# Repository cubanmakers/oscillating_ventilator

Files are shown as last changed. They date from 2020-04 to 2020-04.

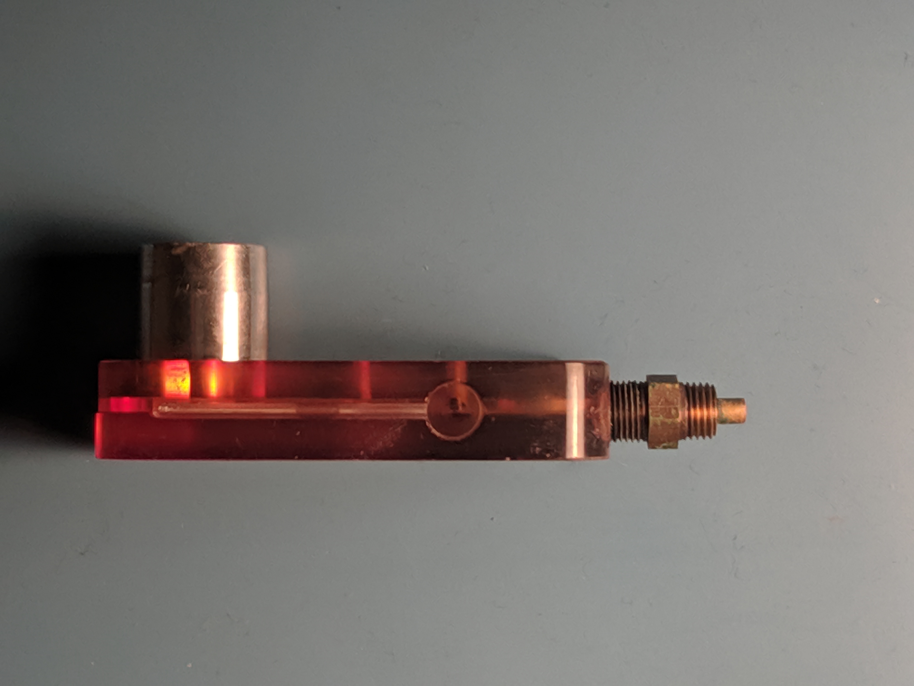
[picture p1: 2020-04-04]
army-ventilator/01_Research/research/izvorski/IMG_20200320_001120.jpg

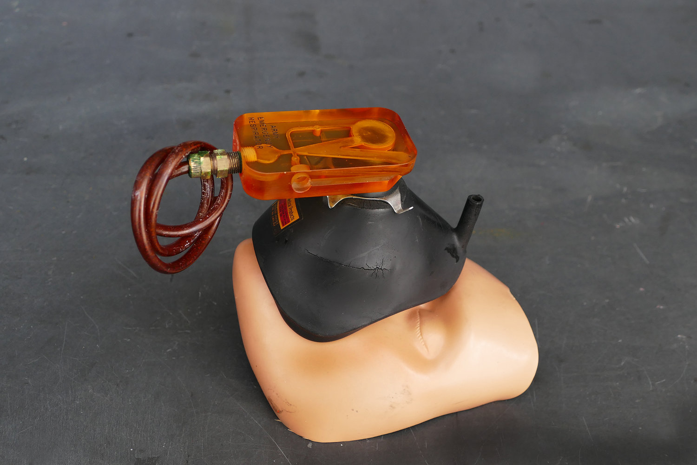
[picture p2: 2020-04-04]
army-ventilator/01_Research/01_Picures/image-asset.jpeg

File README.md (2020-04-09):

# ARMEE Ventilator
Automatic Respiration Management Exclusively for Emergencies

Details and designs for this project are changing rapidly.

Video for overview: https://tinyurl.com/os-vent-vid6

## Communication with team

Join: https://www.helpfulengineering.org/slack
#project-oscillating-ventilator channel

## Designs

* Current preferred design.  See here for files (including solid works): https://github.com/dogcomplex/oscillating_ventilator/tree/0802406738ced803768a7151b4399e3e1ae447ef/army-ventilator/02_Designs/whitney
  * Please read the readme file in that folder^^
* Design doc: https://docs.google.com/document/d/1por1ouQ4hEpHWrM--5hgncuU5_h0UzBLS1P5lqg7H7Q/edit#heading=h.w84bvm9bty9

### Testing request

Team calculated the simplest test should take between 30 to 60 minutes (including set up time) and would be very grateful for the following data:

* Intended Delivered Tidal Volume:  300-500, assess every 100 ml  (simulating patients 50-83 kg, 6 ml/kg )
* Lung Compliance:  10-30, assess every 10 ml/cmH2O
* Airway Resistance: 0-15, assess every 5 cmH2O/l/sec
* Input Pressure (from Source): 50-350, every 75 cmH2O

Recording achieved:  PIP, PEEP, Tidal Volume, Inhale Time, Exhale Time averages over 3 breaths or 10 seconds (feel free to increase time, but not needed)\
Any sequence of these combinations could be aborted when progressing will push past limits of : RR max 30 / min 8,  PIP max 40 / min 10, PEEP max 20 / min 5

Total different max combinations:  3 * 3 * 3 * 5 = 135\
Total time: ~20 seconds * 135 =  45 minutes (plus setup time)

(of course, if you don't mind getting finer grained that would be amazing!)

=====

Bonus from there would be trying different distances between PIP and PEEP, adjusting the calibration screws until PIP - PEEP is 10, 15, 20, 25.  (4 combinations.  89 minutes total)

Finally trying the above for base PEEP of 5, 10, 15, 20  (4 combinations, 6 hours total).  Though this likely have an obvious effect (just increases PIP and PEEP without affecting RR or TV much) in which case - happy to skip entirely!

=====

If that sounds at all reasonable and you have the time to dedicate, please!  Feel free to suggest a better breakdown of tests as well - these are best-guesses, and aimed mainly to inform design rather than certify (though both would be nice).  If there's a proper procedure that covers the same areas faster or better, feel free to use that instead!   And happy to go for even less if you think this is too much or will produce bad data.

Thank you for your consideration and hard work.

### Specification

*This design in relation to the UK British Chambers of Commerce specification:* https://www.britishchambers.org.uk/media/get/Specification%20For%20RMVS%20Challenge.pdf

* Be reliable for 14 days: ⚠ NOT TESTED
* Provide at least two settings for volume of air/air O2 mix delivered per cycle/breath. These settings to be 450ml +/- 10ml per breath and 350ml +/- 10ml per breath. ⛔ NOT IMPLEMENTED
* Provide this air/air O2 mix at a peak pressure of 350 mm H2O. ⚠ NOT TESTED
* Have the capability for patient supply pipework to remain pressurised at all times to 150mm H20. ⚠ NOT TESTED
* Have an adjustable rate of between 12 and 20 cycles/breaths per minute. ⛔ NOT IMPLEMENTED; trade off between _?_ and _?_
* Deliver at least 400ml of air/air 02 mix in no more than 1.5 seconds. The ability to change the rate at which air is pushed into the patient is desirable but not essential. ⚠ NOT TESTED
* Be built from O2 safe components to avoid the risk of fire and demonstrate avoidance of hot spots. ⚠ NOT TESTED
* Be capable of breathing for an unconscious patient who is unable to breathe for his or herself. Ability to sense when a patient is breathing, and support that breathing is desirable but not es- sential. ⚠ NOT TESTED
* Be able to supply pure air and air O2 mix at a range of concentrations including at least 50% and 100% Oxygen. Oxygen shortages are not expected, but the ability to attach a Commercial Off The Shelf (COTS) portable O2 concentrator machine may be a useful feature. ⛔ NOT IMPLEMENTED
* Support connections for hospital Oxygen supplies – whether driven by piped or cylinder infra- structure. ⛔ NOT IMPLEMENTED
* Be compatible with standard COTS catheter mount fittings (15mm Male 22mm Female). ⛔ NOT IMPLEMENTED
* Fail SAFE, ideally generating a clear alarm on failure. Failure modes to be alarmed include (but are not limited to) pressure loss and O2 loss. ⛔ NOT IMPLEMENTED

This requires $~? and ? hours to construct.

This is not suitable to support more than one patient using a splitter valve.

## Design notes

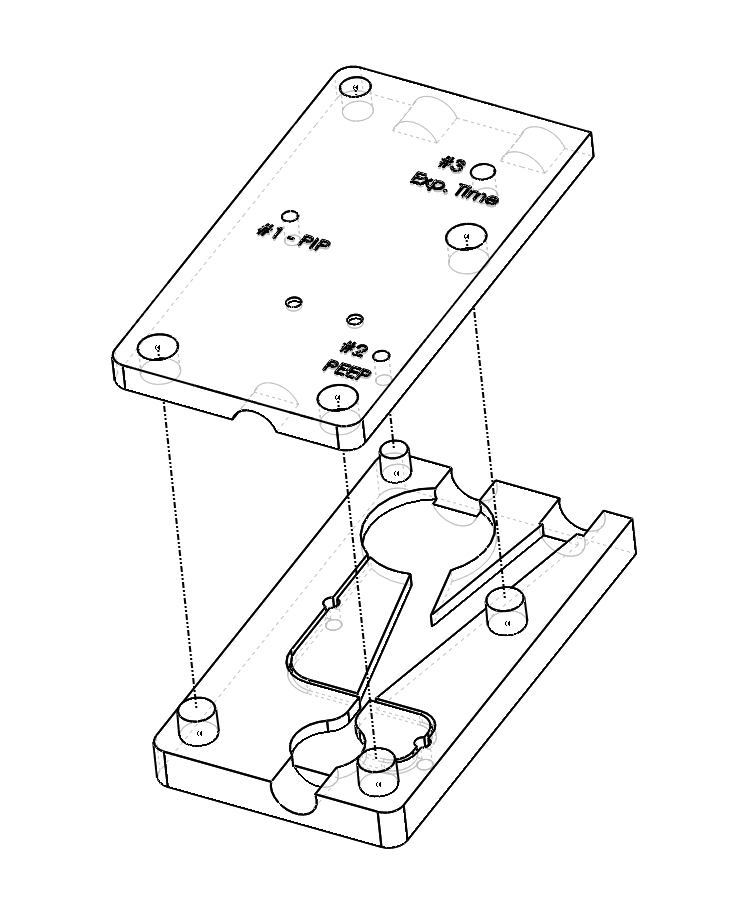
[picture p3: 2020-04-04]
army-ventilator/02_Designs/whitney/Army Vent PEEP 02 Asm.png

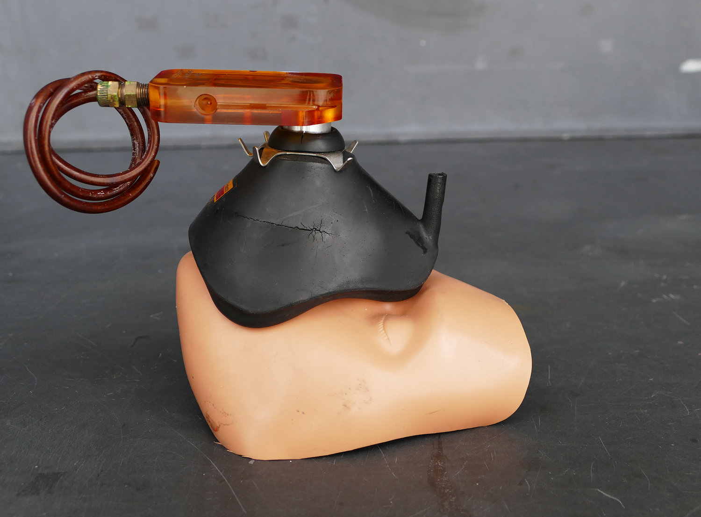
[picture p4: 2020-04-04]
army-ventilator/01_Research/01_Picures/army+emergency+respirator+04.jpg

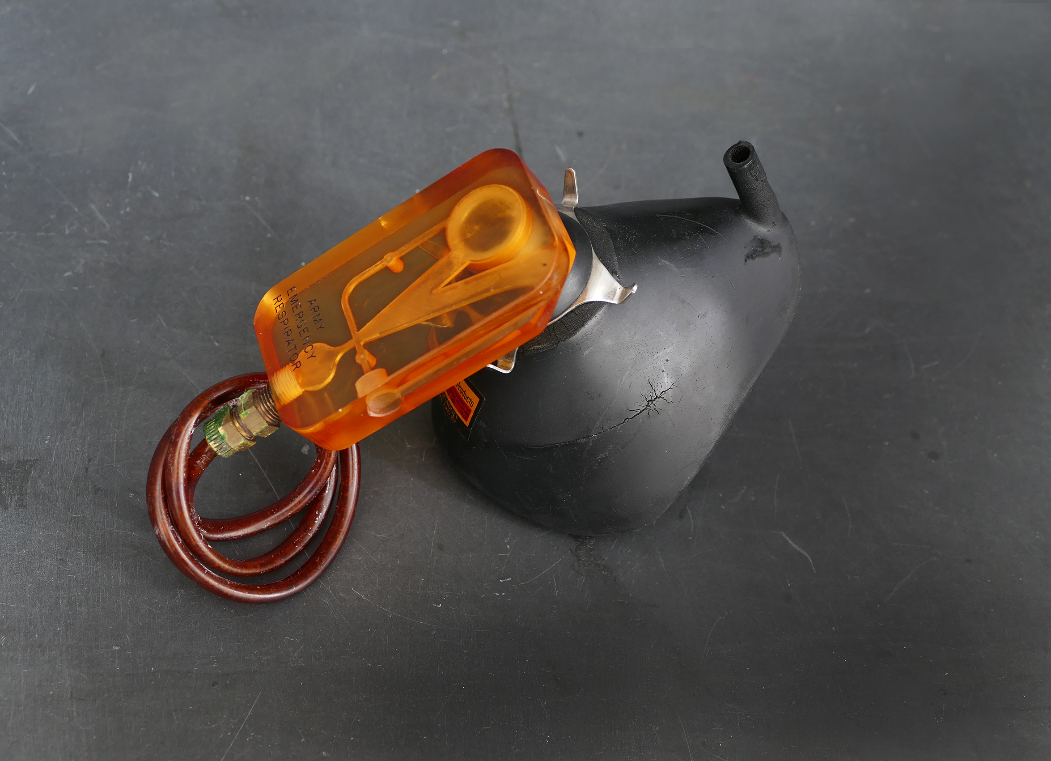
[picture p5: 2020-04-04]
army-ventilator/01_Research/01_Picures/army+emergency+respirator+03.jpg

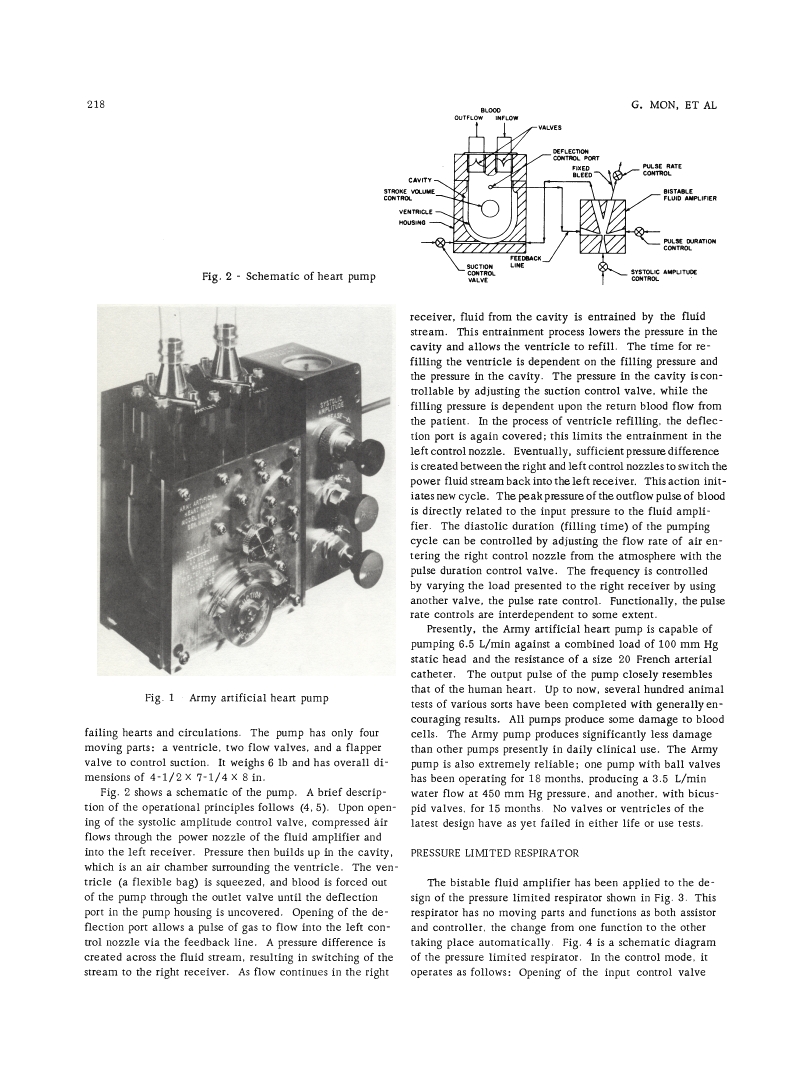
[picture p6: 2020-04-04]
army-ventilator/01_Research/01_Picures/Download (2).jpeg

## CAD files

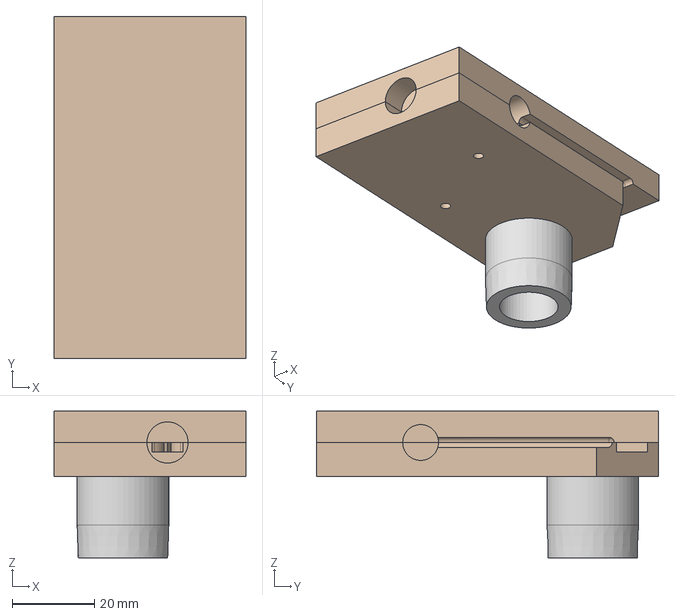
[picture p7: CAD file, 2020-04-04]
army-ventilator/02_Designs/izvorsky/army/Harry_Diamond_Respirator v9.step
46.5 x 83.0 x 35.7 mm

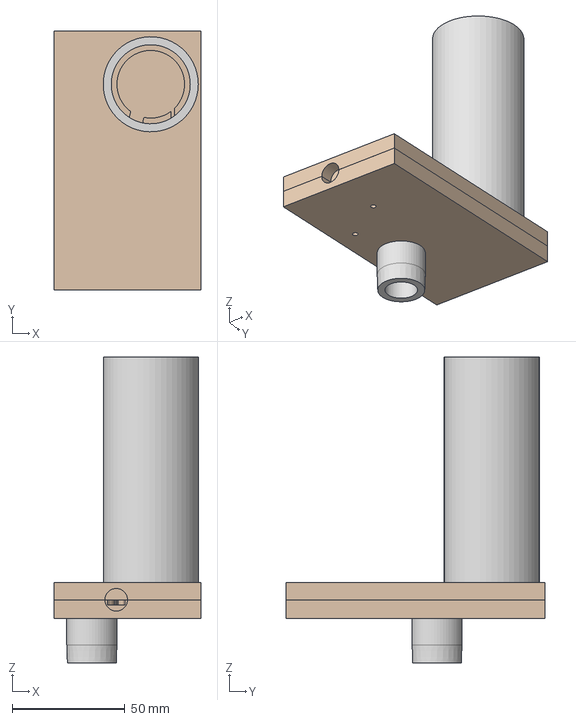
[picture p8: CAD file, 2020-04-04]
army-ventilator/02_Designs/izvorsky/army_peep/Harry_Diamond_PEEP v2.step
65.0 x 115.0 x 135.7 mm

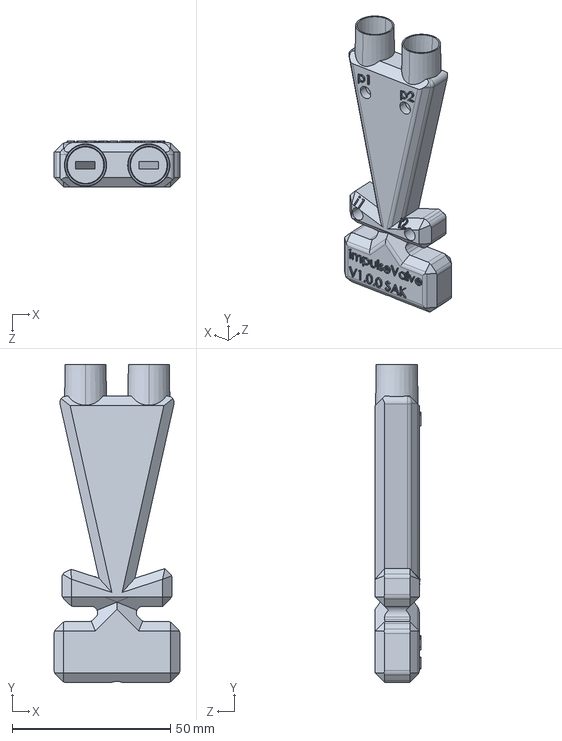
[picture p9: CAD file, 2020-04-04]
army-ventilator/02_Designs/SAK/ImpulseValveV1_0_0.STEP
39.7 x 100.3 x 14.5 mm

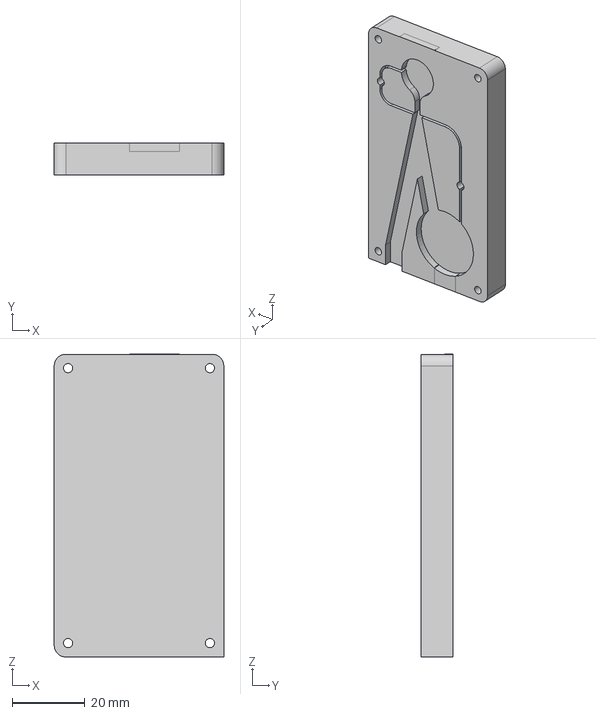
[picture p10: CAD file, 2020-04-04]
army-ventilator/02_Designs/whitney/Army Vent PEEP 02 MACHINABLE REV A v3.step
46.5 x 8.89 x 83.1 mm

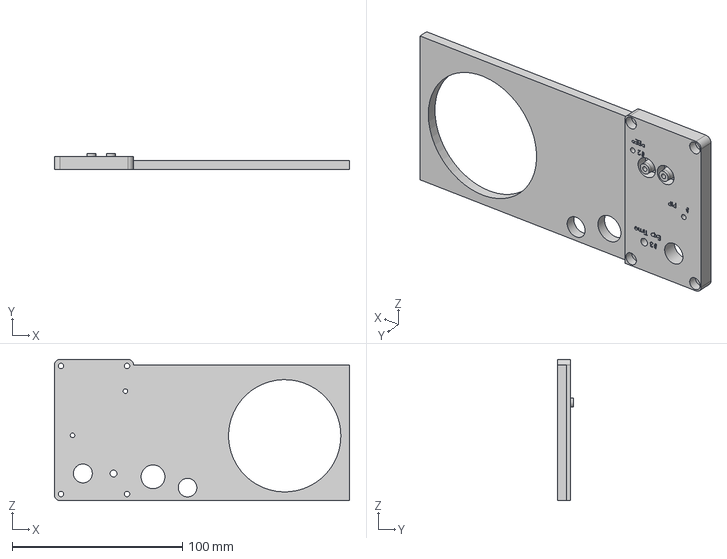
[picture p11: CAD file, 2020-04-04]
army-ventilator/02_Designs/whitney/Army Vent PEEP03 TEST v1.step
173.5 x 9.22 x 83.0 mm

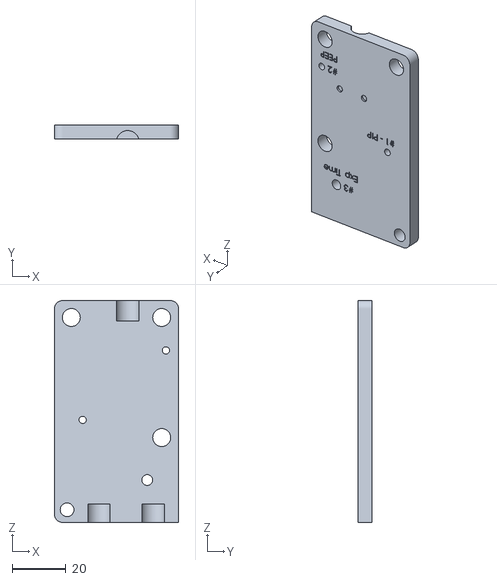
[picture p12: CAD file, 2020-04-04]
army-ventilator/02_Designs/whitney/Army Vent PEEP 02, Lid_20200320.STL
46.5 x 5.16 x 83.0

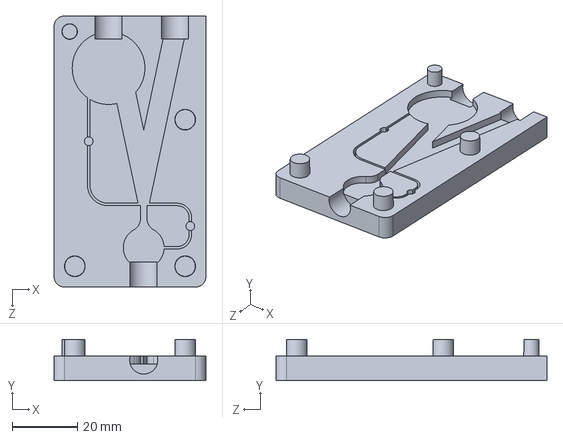
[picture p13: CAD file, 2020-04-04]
army-ventilator/02_Designs/whitney/Army Vent PEEP 02, Body.SLDPRT
46.5 x 12.7 x 83.0 mm

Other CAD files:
army-ventilator/02_Designs/whitney/Army Vent PEEP 02, Lid.sldprt
army-ventilator/02_Designs/whitney/Army Vent PEEP 02, Body_20200320.STL
army-ventilator/01_Research/research/izvorski/Harry_Diamond_Respirator_v4.f3d
army-ventilator/02_Designs/SAK/ImpulseValveV1_0_0.SLDPRT
army-ventilator/02_Designs/SAK/ImpulseValveV1_0_0.STL
army-ventilator/02_Designs/izvorsky/army/Harry_Diamond_Respirator v9.f3d
army-ventilator/02_Designs/izvorsky/army_peep/Harry_Diamond_PEEP v2.f3d
army-ventilator/02_Designs/whitney/Army Vent PEEP 02 MACHINABLE REV A v3.f3d
army-ventilator/02_Designs/whitney/Army Vent PEEP03 TEST v1.f3d

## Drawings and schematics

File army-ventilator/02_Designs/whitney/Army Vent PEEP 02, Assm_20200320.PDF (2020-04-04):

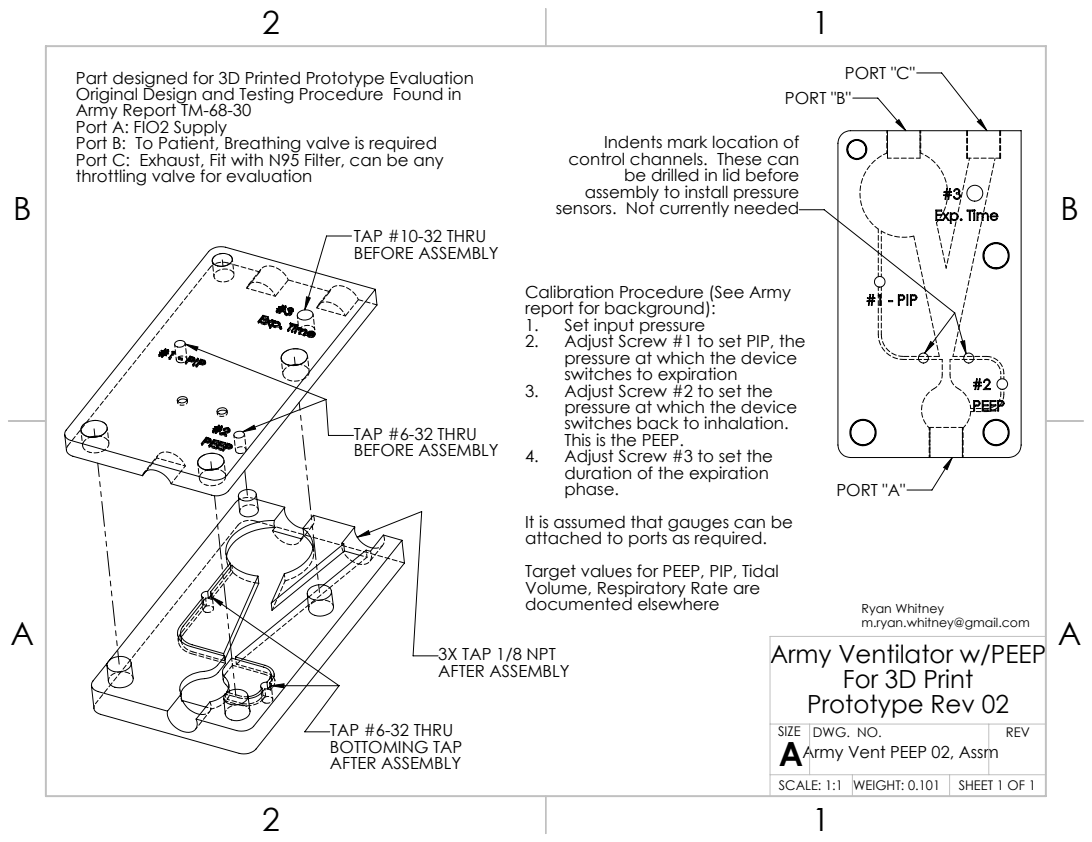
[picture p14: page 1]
PORT "B"; PORT "C"; PORT "A"; TAP #6-32 THRU BEFORE ASSEMBLY; TAP #10-32 THRU BEFORE ASSEMBLY; TAP #6-32 THRU BOTTOMING TAP AFTER ASSEMBLY; 3X TAP 1/8 NPT AFTER ASSEMBLY; documented elsewhere; Ryan Whitney

Part designed for 3D Printed Prototype Evaluation
Original Design and Testing Procedure Found in
Army Report TM-68-30
Port A: FIO2 Supply
Port B: To Patient, Breathing valve is required
Port C: Exhaust, Fit with N95 Filter, can be any
throttling valve for evaluation

Indents mark location of
control channels. These can
be drilled in lid before
assembly to install pressure
sensors. Not currently needed

Calibration Procedure (See Army
report for background):
1. Set input pressure
2. Adjust Screw #1 to set PIP, the
pressure at which the device
switches to expiration
3. Adjust Screw #2 to set the
switches back to inhalation.
This is the PEEP.
4. Adjust Screw #3 to set the
duration of the expiration
phase.
It is assumed that gauges can be
attached to ports as required.
Target values for PEEP, PIP, Tidal
Volume, Respiratory Rate are

m.ryan.whitney@gmail.com
Army Ventilator w/PEEP
For 3D Print
Prototype Rev 02

SIZE A Army Vent PEEP 02, Assm | DWG. NO. | REV

SCALE: 1:1 | WEIGHT: 0.101 | SHEET 1 OF 1

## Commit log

2020-04-04 added alex's models
    [Army Vent PEEP 02, Body.SLDPRT, Army Vent PEEP 02, Body_20200320.STL, Army Vent PEEP 02, Lid.sldprt, Army Vent PEEP 02, Lid_20200320.STL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]
2020-04-04 Chris Jung's modifications for Machining
    [Army Vent PEEP 02 MACHINABLE REV A v3.f3d, Army Vent PEEP 02 MACHINABLE REV A v3.step, Army Vent PEEP03 TEST v1.f3d, Army Vent PEEP03 TEST v1.step]
